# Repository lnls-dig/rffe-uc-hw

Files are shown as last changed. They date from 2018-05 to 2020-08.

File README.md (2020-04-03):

# RFFE microcontroller board

The RFFE microcontroller board is, as the name implies, the digital controller for the fully analog BPM RF Front end boards. It sets the attenuator in both boards, measure the thermometer in each board and sets the DAC for the heater, besides doing all the external communication with external systems by Ethernet.

This board is based on the mBED NXP LPC1768, having the same pinout, processor and ethernet controller. Functionally, the main differences are the addition of a clock generator with spread spectrum capabilities, and a new FeRAM IC for non-volatile fast storage. However, the main difference in this version is that it goes through great measures to avoid generating noise in the 500-MHz frequency range from the Ethernet circuitry, which was detected in the RF BPM for Sirius. Besides the spread spectrum clock for ethernet, shielding, extra power line isolation and layout tweaks were incorporated to ease this problem.

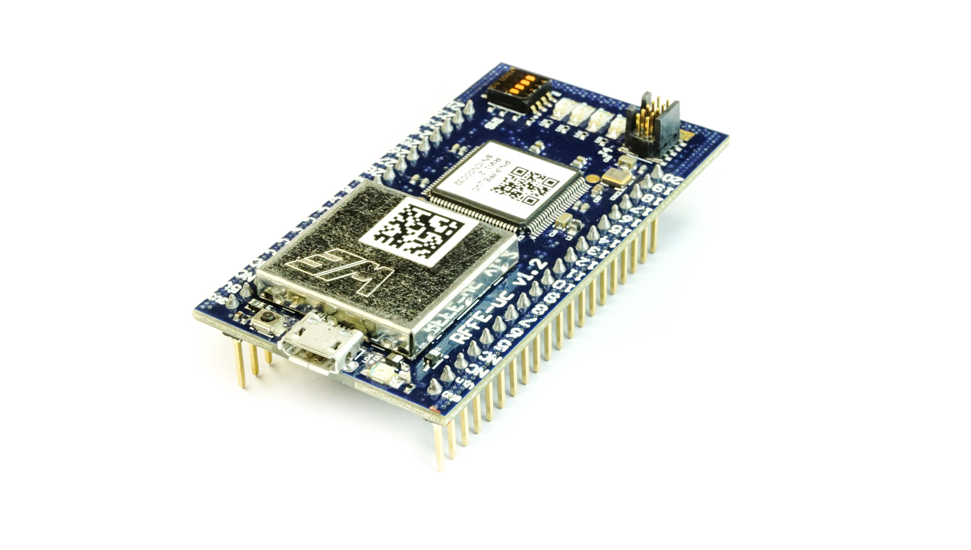
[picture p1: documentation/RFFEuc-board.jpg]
Production board for RFFEuc


Questions about the project, ask Gustavo "Aylons" Bruno (gustavo.bruno at lnls.br).

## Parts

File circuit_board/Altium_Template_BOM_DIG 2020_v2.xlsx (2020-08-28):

BILL OF MATERIALS
Project: |  | Field=ProjectFileName |  |  |  | Rev: | Field=Revision |  | Variant: | Field=VariantName |  |  |  |  | Data: | 21/02/2020
Column=Fitted | Column=Designator | Column=Part Number | Column=Part Description | Column=Value | Column=Tolerance | Column=Voltage | Column=Power | Column=TC | Column=Manufacturer | Column=Manufacturer Part Number | Column=Manufacturer1 Example | Column=Manufacturer1 Part Number | Column=PackageDescription | Column=PressFit | Column=SMD | Column=Socket | Column=Quantity

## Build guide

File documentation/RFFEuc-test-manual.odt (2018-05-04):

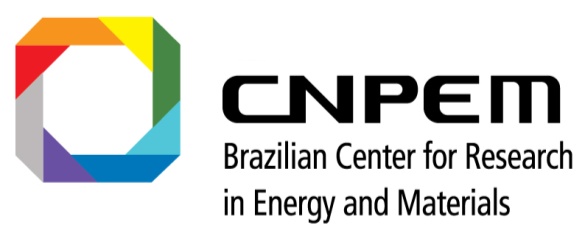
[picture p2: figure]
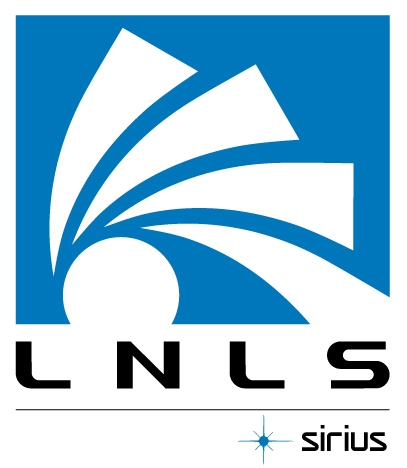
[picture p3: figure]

RFFE-uC

Manual de testes de produção

Laboratório Nacional de Luz Síncrotron - LNLS

Beam Diagnostics Group (DIG)

CERN Open Hardware Licence v1.2 Through this CERN Open Hardware Licence ("CERN OHL") version 1.2, CERN wishes to provide a tool to foster collaboration and sharing among hardware designers. The CERN OHL is copyright CERN. Anyone is welcome to use the CERN OHL, in unmodified form only, for the distribution of their own Open Hardware designs. Any other right is reserved. Release of hardware designs under the CERN OHL does not constitute an endorsement of the licensor or its designs nor does it imply any involvement by CERN in the development of such designs.

Beam Diagnostics Group

Brazilian Synchrotron Light Laboratory

Tel.: +55 19 3512-5071

Email: dig@lnls.br

# Escopo e requisitos do teste

A RFFEuC é uma placa de comunicação e controle para a RFFE, com saídas digitais e sistemas de redução de ruído para evitar que o ruído digital afete as medidas de RF.

Os testes de produção verificam a correta instalação dos principais componentes da placa através de rotinas de auto-teste, loopbacks e interação com uma jiga de testes especificamente projetada e um computador configurado adequadamente. O teste pode ser realizado por somente um operador, que deve operar a jiga e o software.

A estrutura para a realização dos testes consite de:

- Um computador com Ubuntu 16.04 com acesso à uma porta USB e uma interface de rede Ethernet
- Um switch Ethernet com pelo menos dois pontos disponíveis
- Cabo microUSB ligado ao PC, com ponta tipo A
- Jiga de testes RFFEuC_Tester fornecida pelo LNLS
- Programador LPCLink2, ligado à jiga de testes, fornecido pelo LNLS

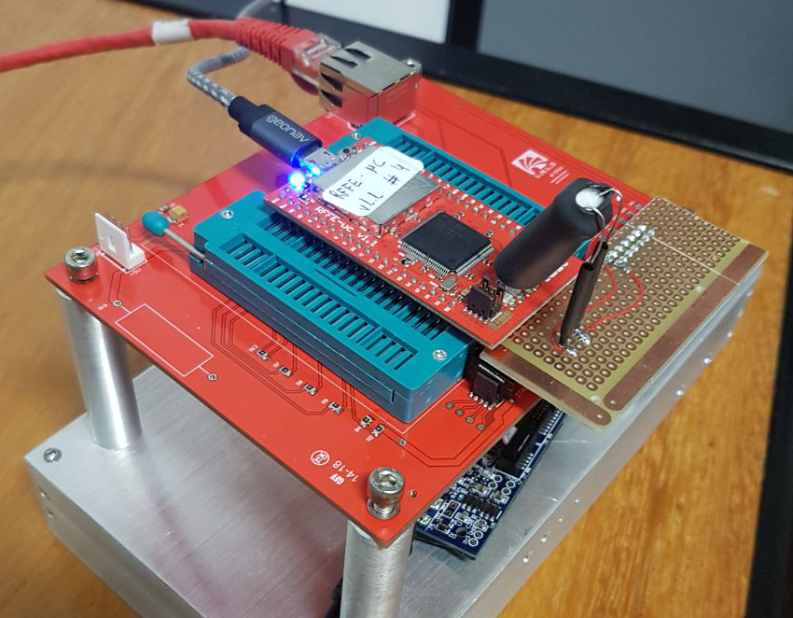
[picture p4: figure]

Figura 1: Jiga de testes RFFE_Tester

A jiga de testes e o PC devem estar devidamente aterrados por uma ligação de baixa impedância. O operador deve seguir procedimentos de proteção contra descargas eletroestáticas durante todo o procedimento.

# Configuração do sistema de testes

Com o sistema Ubuntu 16.04 instalado, é preciso instalar o software LPCXpresso para ter acesso aos drivers do programador do LPCLink2. Para isso, siga os seguintes passos:

1. Acesse o link https://bit.ly/2KoCvgw para ser redirecionado para a página da NXP
2. Crie uma conta (se não tiver uma) e insira suas informações de login
3. Na página redirecionada, clique em “LPCXpresso IDE for Linux v8.x.x”
4. Clique em “Installer_LPCXpresso_8.2.2_650_Linux-x86.tar.gz” para fazer o download do instalador
5. Após o término do download, vá até a pasta em que ele foi salvo e descompacte-o com o comando “tar -xvf Installer_LPCXpresso_8.2.2_650_Linux-x86.tar.gz”
6. Instale as bibliotecas de compatibilidade 32bits necessárias com o comando: “”
7. Execute o instalador extraído com o comando “./Installer_LPCXpresso_8.2.2_650_Linux-x86” (será necessário inserir a senha de administrador)
8. Siga o fluxo de instalação padrão, aceitando os termos da NXP e instale na pasta padrão (/usr/local/lpcxpresso_8.2.2_650)
9. Execute o LPCXpresso: “/usr/local/lpcxpresso_8.2.2_650/lpcxpresso/lpcxpresso”
10. Selecione qualquer pasta para o workspace (irrelevante para o que será utilizado no teste)
11. Uma página web será aberta em seu navegador padrão. Siga as instruções indicadas em “Activating LPCXpresso IDE (Free Edition)” para ativar o LPCXpresso e podermos usar o LPCLink para gravar arquivos maiores que 8KB.

Instale o módulo pylatex e pyserial através dos comandos:

sudo apt-get install python3-pip

sudo pip3 install pylatex

sudo pip3 install pyserial

Faça download do software de testes através do link: https://bit.ly/2jfH8gp e extraia os arquivos em alguma pasta, por exemplo:

rffe (nome arbitrario / pasta raiz)

|-→ rffe-uc-test-bench

|-→ rffe-uc-deploy

|-→ rffe-uc-test-fw

Execute o comando ”sudo adduser $USER dialout” para adicionar o usuário ao grupo dialout (permitir acessar a serial sem permissões de administrador) e relogue na máquina.

Entre na pasta “rffe-uc-test-bench” e dê permissões de execução para o arquivo “rffe_test.py” com o seguinte comando:

chmod +x rffe_test.py

# Preparação do teste

A sequência de serial numbers a serem atribuídos às placas está presente na tabela xxxxx, estes serial numbers devem ser usados sequencialmente durante os testes, queira a placa passe no teste ou não.

Se nenhuma placa foi testada ainda, certifique-se de que o arquivo “ip_sn_table.json” ainda não foi criado na pasta “rffe-uc-test-bench” para evitar conflito na nomenclatura das placas e na execução dos testes.

Conecte o flat cable que está ligado no conector J7 do LPCLink2 ao conector JTAG da placa da jiga de testes (não o conector da placa sendo testada) e fixe o LPCLink2 convenientemente.

Conecte um cabo ethernet no conector RJ45 da jiga de testes e ligue-o ao switch que está sendo utilizado (a subrede deve ser a mesma que o computador que irá rodar o software)

Conecte a placa com o sensor de luminosidade no conector J2 da jiga de testes, mantendo seu posicionamento para baixo (faceando os 4 LEDs da placa a ser testada)

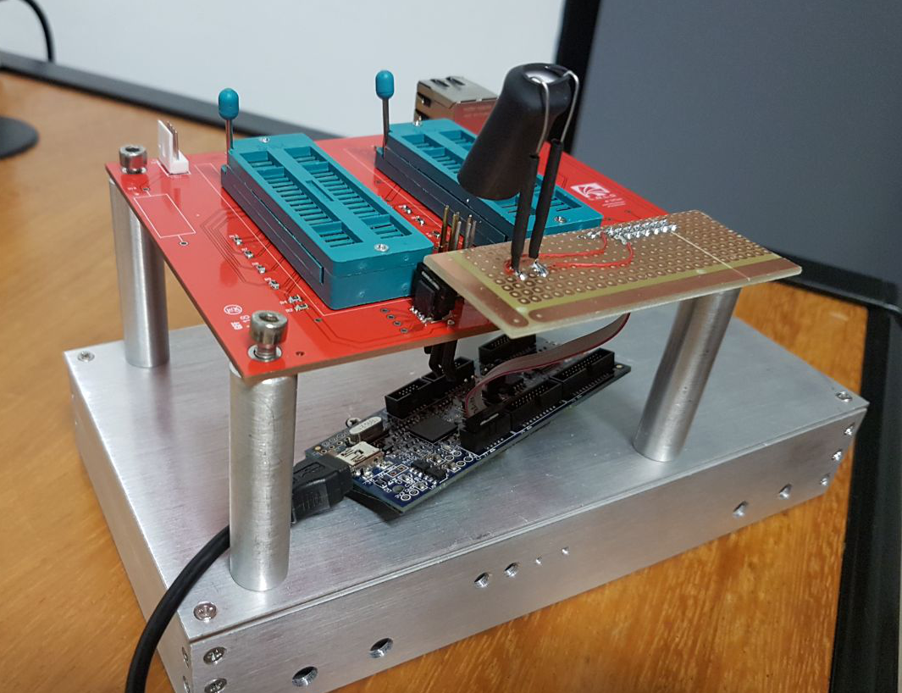
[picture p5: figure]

Figura 2: Jiga com gravador LPCLink2 instalado, sem dispositivo sob teste.

# Execução do teste

Passo | Ação | Detalhamento
1 | Inspeção visual da placa | Verificar presença de resíduos de solda ou outros materiais que possam prejudicar o funcionamento adequado do dispositivo
2 | Ligação do cabo USB | Ligar cabo microUSB no conector adequado do DUT
3 | Instalação na jiga | Montar DUT nos conectores ZIF da jiga. Abaixar as alavancas do ZIF para conexão segura.
4 | Posicionamento do sensor de LED | Posicionar o sensor de sobre os LEDS para a execução do teste.
5 | Iniciar teste automatizado | Executar o software na pasta “rffe-uc-test-bench” com o comando “./rffe_test.py”. (caso o software já esteja sendo executado e as informações mostradas <Serial> <IP> <MAC> estejam corretas, pressione Y e enter para executar o teste)
5.1 | Identificar operador | Inserir o nome do operador e pressionar Enter (este passo só será necessário se esta for a primeira vez executando o software)
5.2 | Identificar placa | Se as informações (default: <Serial> <IP> <MAC>) mostradas pelo software estiverem corretas, pressione N e enter. Caso estejam erradas, pressione Y e enter, inserindo as informações corretas conforme pedidas.
5.3 | Iniciar teste | Para realizar diversos testes seguidos, pressione ‘c’ e enter. Para executá-lo apenas uma vez, pressione ‘o’ e enter
6 | Desconectar cabo USB | Desconectar cabo USB da jiga de testes
7 | Remoção da DUT na jiga | Levantar alavancas dos conectores ZIF. Remover DUT da jiga de testes.
8 | Embalar DUT | Embalar DUT em embalagem apropriada, identificada com número de série.

Observações sobre o software de testes:

- O script guarda um histórico das placas já testadas no arquivo “rffe-uc-test-bench/ip_sn_table.json” e faz a associação dos IPs, serial number e MAC addresses automaticamente. Assim, não é preciso rodar todos os testes de uma só vez, desde que este arquivo esteja íntegro.
- Se uma placa falhar no teste por qualquer motivo, será gravado o IP padrão de “192.168.2.220”, que deve ser sobrescrito futuramente.
- Para placas de reserva, o IP também deve ser o padrão “192.168.2.220”
- Os serial numbers e MAC Addresses são únicos para cada placa, mas os IPs irão se repetir periodicamente e não ficarão pareados, isto é devido ao sistema em que serão utilizadas.

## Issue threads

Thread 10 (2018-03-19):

### ISSUE TITLE
Include MAC Address EEPROM

### ISSUE THREAD

**Issue by henrique-silva** [lnls-dig/rffe-uc-hw#10]
On MBED board, the MAC address is retrieved by a semihost call to the other controller on the board (the one that implements the filesystems), as explained [here](https://os.mbed.com/forum/mbed/post/4680/). Since we don't have this controller on our project, we need a different way to generate a valid MAC Address.

We can use the common [Microchip 24AAxx EEPROMs](https://www.microchip.com/design-centers/memory/serial-eeprom/getting-started/with-mac-address-chips), which are also used in the AFC board.

**Comment by aylons** [comment]
Tested and functional

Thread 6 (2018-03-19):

### ISSUE TITLE
LED pins on PHY chip must be configured via pull resistors

### ISSUE THREAD

**Issue by henrique-silva** [lnls-dig/rffe-uc-hw#6]
According to the PHYTER DP83848J [datasheet](http://www.ti.com/lit/ds/symlink/dp83848j.pdf) page 30, the LEDs that are driven by the PHY (LED_LINK and LED_SPEED) must be configured via pull-up or down resistors to act as a active high/low driver.

For our hardware, since the [RFFE controller board](https://github.com/lnls-dig/rffe-hw) uses common cathode configurations for the ethernet connector LEDs, we need the PHY to be a active-high driver, i.e., there must be a 2k2 pull-down resistor on the LED pins.

These pins don't need to be routed to the LPC1768, since it can't configure the PHY LED drivers, according to this information on the datasheet:

> AN0 (LED_LINK) AN1(LED_SPEED):
> The value on these pins are set by connecting them to GND (0) or VCC (1) through 2.2-k Ω resistors.
> These pins should NEVER be connected directly to GND or VCC.

The Auto-negotiation function of these pins is irrelevant. The LPC firmware overrides this option writing  the needed information directly on PHY registers.

**Comment by aylons** [comment]
Done in v1.1

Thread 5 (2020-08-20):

### ISSUE TITLE
Serial communication resets LPC1769

### ISSUE THREAD

**Issue by aylons** [lnls-dig/rffe-uc-hw#5]
Due to the way the software drives the USB IC DTR, the IC does not work in serial mode because USB DTR keeps reseting the chip. Another connection between IC2 and IC5 should be devised for that.

**Comment by henrique-silva** [comment]
This problem happens because the USB-to-Serial converter is configured to assert the DTR and RTS lines when a communication port is open by the host's driver. If the DTR line is connected directly to the Reset pin, it  will keep the reset signal asserted as long as the serial port is open.

Since we're using the [lpc21isp](https://github.com/domenpk/lpc21isp) software to program the LPC using the serial port, we're able to change the code a little and control the RTS and DTR lines independently. These changes will be committed to a new fork in the lnls-dig repository.
This customization is needed because the LPC1768 needs to have P2.10 pin set to ground after reset in order to enter ISP programming mode.

The connection logic should be:

- LPC Reset = [DTR] XNOR [RTS]
- P2.10 = NOT [RTS]

LPC1768 pins are 5V tolerant, so we can use standard TTL logic.

The meaning of each USB line (DTR and RTS) combination will be explained on the programmer software commit.

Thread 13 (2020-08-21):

### ISSUE TITLE
EEPROM and FeRAM chips have the same slave address

### ISSUE THREAD

**Issue by henrique-silva** [lnls-dig/rffe-uc-hw#13]
Both these chips have the slave address defined as `0b1010xxx`. The EEPROM ignores the last 3 bits, but the FeRAM uses them as the most significant bits of the internal address register.
We can control which one we'll write using the WP bit of the FeRAM, but we can't be sure which one will respond to a read command, since both will only acknowledge the upper 4 bits of the slave address.

**Comment by augustofg** [comment]
To solve this I propose moving the 24AA02E48 EEPROM to the I2C0 bus (same of the CDCE906PW PLL). Both devices addresses differ in the first 4 bits so it should work fine.

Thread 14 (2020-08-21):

### ISSUE TITLE
LPC booting into ISP mode after quick power reset

### ISSUE THREAD

**Issue by henrique-silva** [lnls-dig/rffe-uc-hw#14]
After a quick power-off/power-on the controller boots in ISP mode, waiting for new programming commands, not booting the application firmware.
This can be a problem since this hardware is not connected on a no-break in production environment.
The problem most likely is in the RTS/DTR logic circuitry, probably an unknown initial state.

**Comment by augustofg** [comment]
The DTR and RTS pins are floating when the CP2102 isn't powered (USB disconnected). This causes the RTS and DTR lines to build charge and go to HIGH.

Due the 1uF capacitor in the LPC_RESET line the microcontroller will reset after USB_RTS is already HIGH (forcing P2.10 to low) and the ROM bootloader will enter ISP and watch UART0 for commands.

This also happens when the RFFE uC board is cold enough (I tested this with a freeze spray and could get repeatable results).

Ensuing a remote reset command through the TCP would also make the board reset and enter bootloader ISP sometimes with the newer firmware before https://github.com/lnls-dig/rffe-uc-fw/commit/e7ffb1afbac407f47f27d8d67d6db6e563afe9d5 .

The older firmware didn't exhibited this behavior becaused it used the watchdog to cause a reset, but it never cleared the WDTOF flag. An interesting side effect resulting from this was that the bootloader would never enter in ISP mode again until the RFFE suffered a power cycle (check the LPC176x/5x User Manual rev 4.1, chapter 32 Boot process flowchart, page 630). While WDTOF was set, lpc21isp wouldn't be able to force the microcontroller into ISP mode.

The last release of the new firmware sets the WDTOF flag before resetting the microcontroller through the SYSRESETREQ flag in the [AICR register](http://infocenter.arm.com/help/index.jsp?topic=/com.arm.doc.dui0552a/Cihehdge.html) and immediately clears WDTOF after resetting. In that way the software reset never enters ISP mode, but lpc21isp still can put the microcontroller in ISP mode.

Anyway, the fix is simple. Soldering two 1k pull-down resistors in the USB_DTR and USB_RTS lines fix the problem.

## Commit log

2017-08-04 Initial schematic design
    [rffe-microcontroller.PrjPcb, rffe-microcontroller.SchDoc]
2017-11-02 Changed 12Mhz osc position in schematic for clarity
    [rffe-microcontroller.SchDoc]
2017-11-02 Connected PHY LED pins directly to LED output
    [rffe-microcontroller.SchDoc]
2017-11-09 Added discrete filters to alleviate 500MHz noise
    [rffe-microcontroller.SchDoc]
2017-11-09 Corrected TXD1_PHY net name in IC6 pin
    [rffe-microcontroller.SchDoc]
2017-11-09 Reconnected J1 ground
    [rffe-microcontroller.SchDoc]
2017-11-09 Added power input filter
    [rffe-microcontroller.SchDoc]
2017-11-09 Corrected minor connectivity issues
    [rffe-microcontroller.SchDoc]
2017-11-09 Added several bypass caps
    [rffe-microcontroller.SchDoc]
2017-11-10 Pulled down unused IC6 pins
    [rffe-microcontroller.SchDoc]
2017-11-16 First placement, changed some parts for fitness
    [rffe-microcontroller.PrjPcb, rffe-microcontroller.SchDoc, rffe-uc.PcbDoc]
2017-11-23 First part of layout
    [rffe-microcontroller.PrjPcb, rffe-microcontroller.SchDoc]
2017-11-23 Change net on R20 to USB_VBUS and traced some nets
    [rffe-microcontroller.SchDoc]
2017-11-24 Routed signal NETs and placed vias cap filter
    [rffe-microcontroller.SchDoc]
2017-11-27 chance IC4 to LM3940IMP-3.3/NOPB
    [rffe-microcontroller.SchDoc]
2017-11-27 added polygon Pour on TOP and Bottom layers and change position USB
    [rffe-microcontroller.SchDoc]
2017-11-27 Added Ferroram in both sch and pcb
    [rffe-microcontroller.SchDoc]
2017-12-04 starting DRC process
    [rffe-microcontroller.PrjPcb, rffe-microcontroller.SchDoc]
2017-12-05 DRC corrected errors
    [rffe-microcontroller.PrjPcb, rffe-microcontroller.SchDoc]
2017-12-06 warning msg resolved
    [rffe-microcontroller.SchDoc]
2017-12-06 Added managing marks and name of PCB on V1.0
    [rffe-microcontroller.SchDoc]
2017-12-07 Added mask solder opening on layer numbering
    [rffe-microcontroller.PrjPcb]
2018-01-17 Added via shielding in board perimeter
2018-01-17 Changed reset capacitor
    [rffe-microcontroller.SchDoc]
2018-01-18 Removed filters between LPC and PHY
    These filters were added to check if the 500MHz noise originated from
    the transmission lines, or if they were transmitted via LPC. They were
    changed for a 0ohm resistor in the prototyped and ruled unecessary.
    [rffe-microcontroller.SchDoc]
2018-01-25 Added tested EMC protection to PHY IC.
    Added capacitors and resistors to PHY pins as specified by tests.
    [rffe-microcontroller.PrjPcb, rffe-microcontroller.SchDoc]
2018-01-25 Changed C35 to a smaller footprint
    [rffe-microcontroller.SchDoc]
2018-01-26 Addwed spread spectrum clock circuit
    According to issue #9, a spread spectrum clock synthesizer was added,
    substituting the 50MHz clock.
    [rffe-microcontroller.PrjPcb, rffe-microcontroller.SchDoc]
2018-01-28 Added logic between USB serial and LPC
    This enables both programming and serial console and is described in
    detail in issue #5
    [rffe-microcontroller.SchDoc]
2018-01-28 Added common mode choke to board
    This helps with noise comming from the PHY, as in issue #3
    [rffe-microcontroller.SchDoc]
2018-01-28 Added IC9 - MAC Address EEPROM
    This will solve issue #10
    [rffe-microcontroller.SchDoc]
2018-01-28 Changed USB connector for newer part
    The older part was obsolete, as described in issue #2. The new part is
    also more easily available than the reversed option.
    [rffe-microcontroller.SchDoc]
2018-01-28 Started layout process for version 1.1
    [rffe-microcontroller.SchDoc]
2018-01-30 All components placed, still no DRC
    [rffe-microcontroller.SchDoc]
2018-01-31 Changed capacitors C61, C62, C63, C64 e C65 to 100pF and C34 and C38 to 68pF. Imported this changes to PCB. Changed Capacitors_LNLS.mdb to right database.
    [rffe-microcontroller.PrjPcb, rffe-microcontroller.SchDoc]
2018-02-01 Changed IC7 part number to the right P/N
    [rffe-microcontroller.SchDoc]
2018-02-01 Removed a short circuit on the PCB layout
    [rffe-microcontroller.SchDoc]
2018-02-01 Connected GND pin of two components that were unconnected
    [rffe-microcontroller.SchDoc]
2018-02-02 Added output pins names to silk on the PCB
2018-02-06 Added draftsman file
    [rffe-microcontroller.PrjPcb]
2018-02-08 Added manufacturing documentation generators
    [rffe-microcontroller.PrjPcb, rffe-microcontroller.SchDoc]
2018-02-08 Corrected details on OutputJob
    [rffe-microcontroller.PrjPcb]
2018-02-23 Changed the positions of JTAG test points on the PCB. Changed the test points on Schematic and PCB to others with bigger pad. Before, it was a pad with 1.2mm diameter and now, it is a pad with 1.5mm 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
    [rffe-microcontroller.PrjPcb, rffe-microcontroller.SchDoc]
2018-03-02 Changed JTAG test points with 1.5mm diameter to test points with 1.2mm diameter.
    [rffe-microcontroller.SchDoc]
2018-03-02 Updated PCB with 3d model of some components: USB connector (J3) and mode choke (L8 and L9). Please enter the commit message for your changes. Lines starting
2018-03-19 Added pullup resistors to layout
2018-03-19 Adjusted the silk of the board on the connector pins
2018-03-19 Adjusted the silk on power pins of the connector.
2018-03-20 Added pullup to SMBUS lines
    This fixes bug #12
    [rffe-microcontroller.SchDoc]
2018-03-20 Updated version number for 1.2
    [rffe-microcontroller.SchDoc]
2018-03-22 Corrected J4 connector for -K option
    [rffe-microcontroller.SchDoc]
2018-04-27 Added attention points to top side assembly sheet
2020-08-20 Added R48 and R49 1K #14
    Added R48 and R49 1K 0402 RTS / DTR to Pull Down.
    [rffe-microcontroller.SchDoc]
2020-08-21 Change value R10;R30;R44;R45 to 2K2
    Change value R10 ; R30 ; R44 ; R45 10K to 2K2.
    [rffe-microcontroller.SchDoc]
2020-08-21 Change I2C channel for PLL #13
    Change I2C channel IC9 FeRAM_SDA to PLL_SDA and FeRAM_SCL to PLL_SCL.
    Repair USB PAD for more solder area
    [rffe-microcontroller.PrjPcb]
2020-08-22 Updated license to OHL2
    [rffe-microcontroller.SchDoc]
2020-08-22 change designator R48 to R50
    [rffe-microcontroller.SchDoc]
2020-08-28 BOM Template xls
    new version for BOM template
    [Altium_Template_BOM_DIG 2020_v2.xlsx]
